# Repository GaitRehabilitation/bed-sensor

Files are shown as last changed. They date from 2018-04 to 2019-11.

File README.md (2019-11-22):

# Bed Sensor

## Background

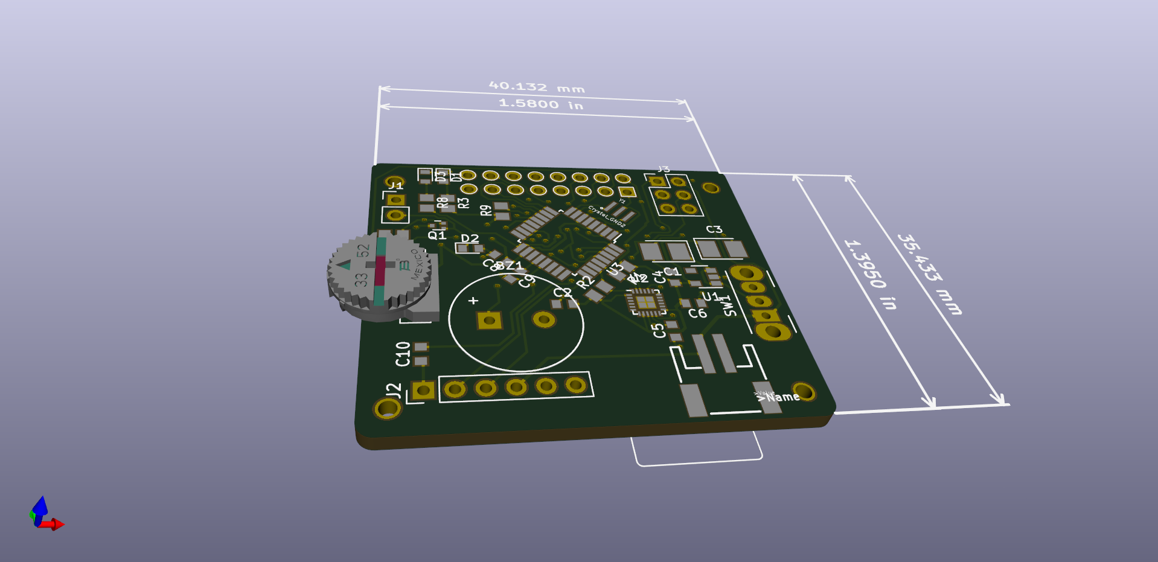
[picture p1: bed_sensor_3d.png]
bed sensor


This sensor is built around the open source schematic of the Ardunio Pro Mini and the seperate parts we're tested sepertly and the final board was printed from [oshPark](https://oshpark.com/). This is an experemential sensor that makes sure patients roll over within a fixed interval. The model uses a state machine with two states: COUNTING_STATE, and a ROTATING_STATE. The counting state samples the direction of the acceleration vector and during the ROTATING_STATE, the arc angle between the current vector and the sampled data from the counting state determins the rotation of the device from the resting state. A average filter is sampled from the current resting angle of the sensor is sampled by taking 20% of the current sample vector and 80% of the current resting angle. This is a mitigation strategy that avoids sampling from sudden movments and affecting the angle of the sensor. The counting state is reset if the devaition from the scalar vector is greater then .35 g's.  

## Programming

Tools:
- [SCONS](https://scons.org/)
- [avrdud](https://www.nongnu.org/avrdude/)
- [avr-gcc](https://gcc.gnu.org/wiki/avr-gcc)
- [minicore](https://github.com/MCUdude/MiniCore)

building cpp code `scons build`. The compiled code produces a hex 

```avrdude -c <programmer> -p atmega328 -b 57600  -U flash:w:main.hex -U lfuse:w:0xff:m -U hfuse:w:0xd1:m -U efuse:w:0xff:m```

![avr fuse](./fuse_bits.png)

[Fuse Calculator](http://eleccelerator.com/fusecalc/fusecalc.php?chip=atmega328p)

## Maintainers

The current maintainers of this repository are:

* Michael Pollind <polli104@mail.chapman.edu>

# License

```
/**
* Copyright 2018 GaitRehabilitation
*
* Licensed under the Apache License, Version 2.0 (the "License");
* you may not use this file except in compliance with the License.
* You may obtain a copy of the License at
*
*     http://www.apache.org/licenses/LICENSE-2.0
*
* Unless required by applicable law or agreed to in writing, software
* distributed under the License is distributed on an "AS IS" BASIS,
* WITHOUT WARRANTIES OR CONDITIONS OF ANY KIND, either express or implied.
* See the License for the specific language governing permissions and
* limitations under the License.
*/

```

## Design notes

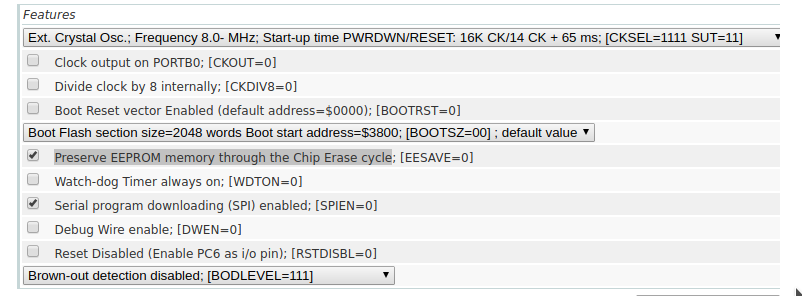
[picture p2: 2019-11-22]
fuse_bits.png

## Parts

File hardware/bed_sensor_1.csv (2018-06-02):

Id | Designator | Package | Quantity | Designation | Supplier and ref
1 | U5 | CFAH0802D-YYH-JP | 1 | CFAH0802D-YYH-JP | https://www.crystalfontz.com/product/cfah0802dyyhjp-8x2-sunlight-readable-character-lcd
2 | BZ1 | PS1240P02BT | 1 | Buzzer | https://www.mouser.com/ProductDetail/TDK/PS1240P02CT3?qs=sGAEpiMZZMs%252b6Ea5iKw4JoP%2fJ%2fqwrEG3
3 | C1 | CP_Tantalum_Case-T_EIA-3528-12_Reflow | 1 | 10uF | https://www.mouser.com/ProductDetail/81-GRM33C80J104KE15D
4 | C2 | C_0603_1608Metric | 1 | 10nF | https://www.mouser.com/ProductDetail/80-C0603X103J4HACTU
5 | C3 | CP_Tantalum_Case-B_EIA-3528-21_Reflow | 1 | 10uF | https://www.mouser.com/ProductDetail/81-GRM33C80J104KE15D
6 | C4,C5 | C_0603_1608Metric | 2 | .1uF | https://www.mouser.com/ProductDetail/81-GRM032R60J104KE5D
7 | C6 | C_0603_1608Metric | 1 | 1uF | https://www.mouser.com/ProductDetail/81-GRM032R60J104KE5D
8 | C7 | C_0603_1608Metric | 1 | 10uF | https://www.mouser.com/ProductDetail/81-GRM33C80J104KE15D
9 | C8,C9,C10 | C_0603_1608Metric | 3 | .1uf | https://www.mouser.com/ProductDetail/81-GRM032R60J104KE5D
10 | D1 | LED_0603_1608Metric | 1 | LED | https://www.mouser.com/ProductDetail/Kingbright/APT1608ZGCK?qs=sGAEpiMZZMuCm2JlHBGefut9Bg6HSmgVetA7n4GwW1U%3d
11 | D2 | D_0603_1608Metric | 1 | D | https://www.mouser.com/ProductDetail/755-RB162VAM-20TR
12 | J1 | PinHeader_1x02_P2.54mm_Vertical | 1 | Conn_01x02
13 | J2 | PinHeader_1x06_P2.54mm_Vertical | 1 | Conn_01x06
14 | J3 | PinHeader_2x03_P2.54mm_Vertical | 1 | ISP
15 | JP1 | SolderJumper-2_P1.3mm_Open_Pad1.0x1.5mm | 1 | Jumper_NO_Small
16 | L1 | L_Taiyo-Yuden_NR-40xx | 1 | 10uH | https://www.mouser.com/ProductDetail/Murata-Electronics/LQH32CN100K53L
17 | Q1 | SOT-723 | 1 | 2N2219 | https://www.mouser.com/ProductDetail/ON-Semiconductor/NSVMMBT2222AM3T5G
18 | Q2,Q3 | SOT-23 | 2 | BSS138 | https://www.mouser.com/ProductDetail/ON-Semiconductor-Fairchild/BSS138?qs=sGAEpiMZZMvlOED0T0kTWl5MKyjMqq%2fg
19 | R1,R2,R3,R6,R7,R9 | R_0805_2012Metric | 6 | 10k | https://www.mouser.com/ProductDetail/603-RC0805FR-0710KL
20 | R4 | R_0805_2012Metric | 1 | 1K | https://www.mouser.com/ProductDetail/603-RC0805JR-071KL
21 | R5 | R_0805_2012Metric | 1 | 220 | https://www.mouser.com/ProductDetail/Vishay/CRCW0805220RFKEAC
22 | R8 | R_0805_2012Metric | 1 | 330 | https://www.mouser.com/ProductDetail/652-CR0805-FX3300GLF
23 | RV1 | Potentiometer_Trimmer_ACP_CA9h2.5_Vertical_Px2.5mm_Py5.0mm | 1 | 10K | https://www.amazon.com/MCIGICM-potentiometer-assortment-Breadboard-Potentiometer/dp/B07C3XHVXV?s=industrial
24 | SW1 | SW_CuK_OS102011MA1QN1_SPDT_Angled | 1 | SW_SPST | https://www.mouser.com/ProductDetail/611-OS102011MA1QN1
25 | U1 | SOT-23-5 | 1 | MIC5205-3.3 | https://www.mouser.com/ProductDetail/Microchip-Technology-Micrel/MIC5205-33YM5-TR
26 | U2 | QFN-24-1EP_3x3mm_P0.4mm_EP1.75x1.6mm | 1 | MPU-9250 | https://www.mouser.com/ProductDetail/TDK-InvenSense/MPU-9250
27 | U3 | SOIC-14_3.9x8.7mm_P1.27mm | 1 | TXB0104D | https://www.mouser.com/ProductDetail/Texas-Instruments/TXB0104D
28 | U4 | SOT-363_SC-70-6 | 1 | LTC3525-5 | https://www.mouser.com/ProductDetail/Analog-Devices-Linear-Technology/LTC3525ESC6-5TRPBF
29 | Y1 | OSC_CSTCE8M00G55-R0 | 1 | Crystal_GND2 | https://www.mouser.com/ProductDetail/81-CSTCE8M00G55-R0
30 | D3 | LED_0603_1608Metric_Pad0.67x1.00mm_HandSolder | 1 | LD271 | https://www.mouser.com/ProductDetail/Kingbright/APT1608VBC-D?qs=sGAEpiMZZMuCm2JlHBGefut9Bg6HSmgVsfyCYNObiTs%3d
31 | J4 | JSTPH2 | 1 | Conn_01x02 | https://www.adafruit.com/product/1769
32 | U6 | TQFP-32_7x7mm_Pitch0.8mm | 1 | ATMEGA328-AU | https://www.mouser.com/ProductDetail/556-ATMEGA328-AU

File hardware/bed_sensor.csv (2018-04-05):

Id | Designator | Package | Quantity | Designation | Supplier and ref
1 | J1 | JSTPH2 | 1 | Conn_01x02 | https://www.adafruit.com/product/1769
2 | J2 | PinHeader_1x06_P2.54mm_Horizontal | 1 | Conn_01x06
3 | J3 | PinHeader_1x02_P2.54mm_Vertical | 1 | Conn_01x02 | https://www.adafruit.com/product/1201
4 | SW1 | SW_CuK_OS102011MA1QN1_SPDT_Angled | 1 | SW_SPST | https://www.mouser.com/ProductDetail/611-OS102011MA1QN1
5 | uP1 | ArduProMini | 1 | ARDUPROMINI
6 | RV1 | Potentiometer_ACP_CA6-H2,5_Horizontal | 1 | 10K | https://www.mouser.com/ProductDetail/Bourns/3310C-001-103L
7 | D1 | D_DO-35_SOD27_P7.62mm_Horizontal | 1 | D
8 | Q1 | TO-92_Inline | 1 | 2N2219
9 | R1 | R_Axial_DIN0207_L6.3mm_D2.5mm_P7.62mm_Horizontal | 1 | 220
10 | R2 | R_Axial_DIN0207_L6.3mm_D2.5mm_P7.62mm_Horizontal | 1 | 1K
11 | BZ1 | MagneticBuzzer_Kingstate_KCG0601 | 1 | Buzzer | https://www.mouser.com/ProductDetail/TDK/PS1240P02CT3?qs=sGAEpiMZZMs%252b6Ea5iKw4JoP%2fJ%2fqwrEG3
12 | DS1 | NHD-0216HZ-FSW-FBW-33V3C | 1 | WC1602A | https://www.mouser.com/ProductDetail/Newhaven-Display/NHD-0216HZ-FSW-FBW-33V3C
13 | J4 | PinSocket_1x08_P2.54mm_Vertical | 1 | Conn_01x08 | https://www.amazon.com/MPU-6050-MPU6050-Accelerometer-Gyroscope-Converter/dp/B008BOPN40

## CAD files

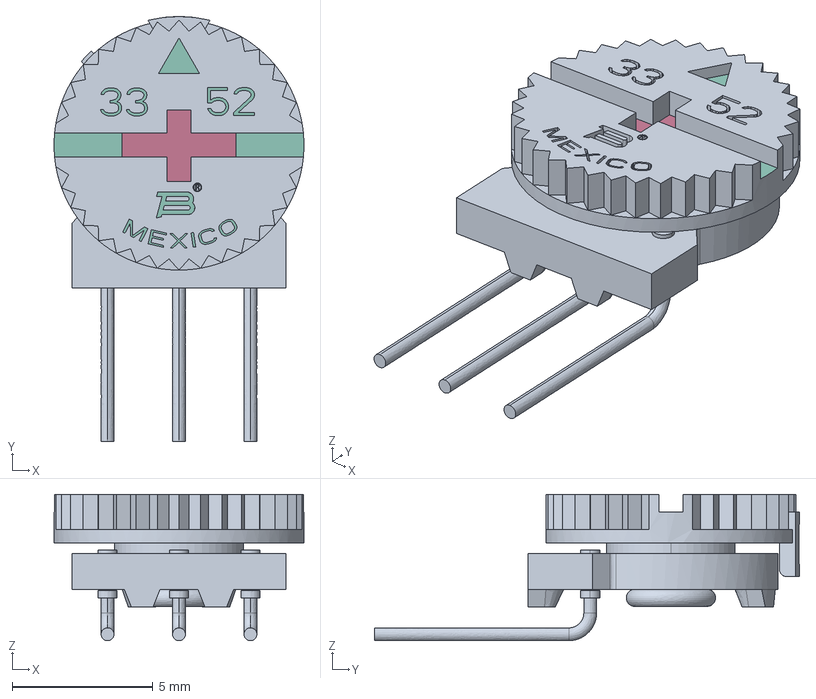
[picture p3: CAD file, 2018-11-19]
hardware/3352W001XXX.stp
8.89 x 15.1 x 5.21 mm

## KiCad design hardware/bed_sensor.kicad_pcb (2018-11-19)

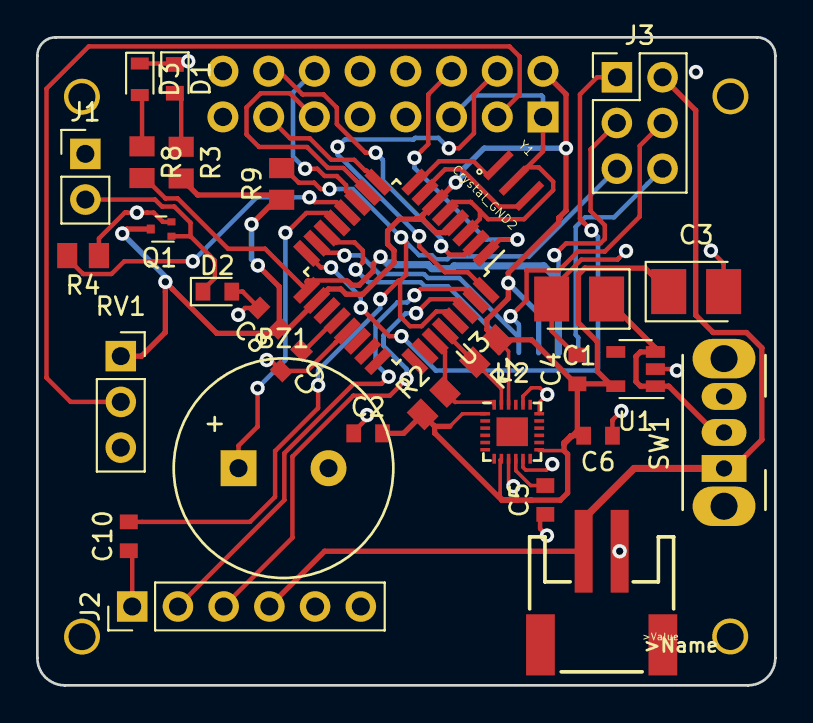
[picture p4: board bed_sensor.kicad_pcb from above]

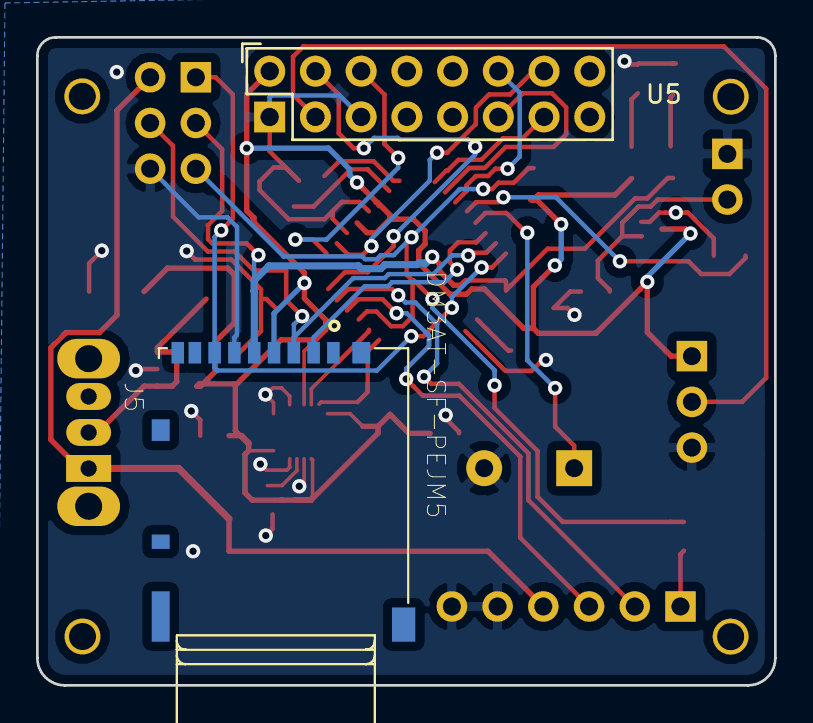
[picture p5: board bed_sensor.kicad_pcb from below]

Board: 2 copper layers, 41.0 x 36.0 mm, 32 parts (2 on the bottom side), 31 nets.

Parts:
BZ1: Buzzer; PS1240P02BT
C1: 10uF; CP_Tantalum_Case-T_EIA-3528-12_Reflow
C2: 10nF; C_0603_1608Metric
C3: 10uF; CP_Tantalum_Case-B_EIA-3528-21_Reflow
C4, C5, C6: .1uF; C_0603_1608Metric
C8, C9, C10: .1uf; C_0603_1608Metric
D1: LED; LED_0603_1608Metric
D2: D; D_0603_1608Metric
D3: LD271; LED_0603_1608Metric_Pad0.67x1.00mm_HandSolder
J1: Conn_01x02; PinHeader_1x02_P2.54mm_Vertical
J2: Conn_01x06; PinHeader_1x06_P2.54mm_Vertical
J3: ISP; PinHeader_2x03_P2.54mm_Vertical
J4: Conn_01x02; JSTPH2
J5: DM3AT-SF-PEJM5; HRS_DM3AT-SF-PEJM5
Q1: 2N2219; SOT-723
R1, R2, R3, R9: 10k; R_0805_2012Metric
R4: 1K; R_0805_2012Metric
R8: 330; R_0805_2012Metric
RV1: 10K; PinSocket_1x03_P2.54mm_Vertical
SW1: SW_SPST; SW_CuK_OS102011MA1QN1_SPDT_Angled
U1: MIC5205-3.3; SOT-23-5
U2: MPU-9250; QFN-24-1EP_3x3mm_P0.4mm_EP1.75x1.6mm
U3: ATMEGA328-AU; TQFP-32_7x7mm_P0.8mm
U5: CFAH0802D-YYH-JP
Y1: Crystal_GND2; OSC_CSTCE8M00G55-R0

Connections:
+3V3: C2.2, C3.1, C4.1, C6.2, C8.1, J5.4, Q1.3, R1.1, R2.1, R3.2, R9.1, RV1.1, U1.5, U2.1, U2.8, U2.13, U2.22, U3.4, U3.6, U3.18, U5.2
/Ardunio/DTR: C10.1, J2.1
/Ardunio/RESET: C10.2, J3.5, R9.2, U3.29
/Ardunio/RX1: J2.3, U3.30
/Ardunio/TX0: J2.2, U3.31
Buzzer: BZ1.1, U3.13
CS: J5.2, U3.14
DB4: U3.10, U5.11
DB5: U3.11, U5.12
DB6: U3.9, U5.13
DB7: U3.2, U5.14
Display_Enable: U3.1, U5.6
GND: BZ1.2, C1.2, C2.1, C3.2, C4.2, C5.1, C6.1, C8.2, C9.2, D1.1, D2.2, D3.1, J1.1, J2.5, J2.6, J3.6, J4.1, J5.6, RV1.3, U1.2, U2.9, U2.11, U2.18, U2.20, U3.3, U3.5, U3.21, U5.1, U5.5, Y1.2
MISO: J3.1, J5.7, U3.16
MOSI: J3.4, J5.3, U3.15
unnamed: C1.1, SW1.2, U1.1, U1.3
unnamed: C5.2, U2.10
unnamed: C9.1, U3.20
unnamed: D1.2, R3.1
unnamed: D2.1, J1.2, Q1.1
unnamed: D3.2, R8.1
unnamed: Q1.2, R4.1
unnamed: RV1.2, U5.3
unnamed: U3.7, Y1.3
unnamed: U3.8, Y1.1
RS: U3.32, U5.4
SCK: J3.3, J5.5, R8.2, U3.17
SCL_MPU: R1.2, U2.23, U3.28
SDA_MPU: R2.2, U2.24, U3.27
VCC: J2.4, J3.2, J4.2, SW1.1
Vibration: R4.2, U3.12

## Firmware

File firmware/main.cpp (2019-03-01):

#define __AVR_ATmega328__ 1

#include <Arduino.h>
#include <Wire.h>
#include <SPI.h>
#include <SdFat.h>

#include <LiquidCrystal.h>

#define COUNTING_STATE 0
#define ROTATE_STATE 1

#define TARGET_ANGLE 50.0f //degreese
#define TIME 7200000       //milliseconds
#define REMIND_TIME 15000

// PINS ------------------------------------------------------
const int MPU_addr = 0x68;
const int rs = 2, en = 3, d4 = 6, d5 = 7, d6 = 5, d7 = 4;
const int piezoPin = 9;
const int chipSelect = 10;

const char REPOS_MSG[] = {"Re-Pos"};
const char META_FILE[] = {"META.bin"};
// PINS ------------------------------------------------------

LiquidCrystal lcd(rs, en, d4, d5, d6, d7);

unsigned long previous_time = 0;
unsigned long lcd_refresh = 0;
unsigned long display_time = 0;
unsigned long meta_update_time = 0;

float restingX, restingY, restingZ;
float rotationX, rotationY, rotationZ;
float scaledX, scaledY, scaledZ;
float movingAvg = 0.0f;
int count = 0;

byte state = 0;

// LOGGING DATA -----------------------------------------------------------
const uint32_t LOG_INTERVAL_USEC = 10000;
const uint8_t BUFFER_BLOCK_COUNT = 10;
const uint32_t FILE_BLOCK_COUNT = 256000;
const uint8_t ACCEL_DIM = 3;
const uint8_t GYRO_DIM = 3;

//size of the queue
const uint8_t QUEUE_DIM = BUFFER_BLOCK_COUNT + 1;
// Index of last queue location.
const uint8_t QUEUE_LAST = QUEUE_DIM - 1;

bool reset_buzzer = false;
bool reminder_buzzer = false;
bool reset_on_move = false;

//sdfat
SdFat sd;
SdBaseFile binFile;
// SdBaseFile metaFile;
char fileName[13];

struct data_t
{
  uint32_t time;
  int16_t accel[ACCEL_DIM];
  int16_t gyro[GYRO_DIM];
  int16_t temp;
  uint8_t meta;
};

// DATA BLOCK 512 bytes --------------------------------------------------------------------
// Number of data records in a block.
const uint16_t DATA_DIM = (512 - 2) / sizeof(data_t);

//Compute fill so block size is 512 bytes.  FILL_DIM may be zero.
const uint16_t FILL_DIM = 512 - 2 - DATA_DIM * sizeof(data_t);

//data
struct block_t
{
  uint16_t count;
  data_t data[DATA_DIM];
  uint8_t fill[FILL_DIM];
};

bool isResting(float x, float y, float z);
void createBin();
void sdFail(const char *);
float arcAngle(float tx, float ty, float tz, float fx, float fy, float fz);
void acquireData(data_t *data);

void setup()
{
  // wdt_enable(WDTO_2S);
  lcd.begin(16, 2);
  if (!sd.begin(chipSelect, SD_SCK_MHZ(50)))
  {
    sdFail("REQ SD");
  }
  pinMode(piezoPin, OUTPUT);

  restingX = .01f;
  restingY = .01f;
  restingZ = .01f;
  rotationX = .1f;
  rotationY = .01f;
  rotationZ = .01f;

  Wire.begin();
  Wire.beginTransmission(MPU_addr);
  Wire.write(0x6B); // PWR_MGMT_1 register
  Wire.write(0);    // set to zero (wakes up the MPU-6050)
  Wire.endTransmission(true);

  Wire.beginTransmission(MPU_addr);
  Wire.write(0x1C);
  Wire.write(B00001000); //here is the byte for sensitivity (8g here)
  Wire.endTransmission(true);


  Wire.beginTransmission(MPU_addr);
  Wire.write(0x1B);
  Wire.write(B00101000); //here is the byte for sensitivity (1000 degree sec)
  Wire.endTransmission(true);

}

void loop()
{
  createBin();
  
  // Allocate extra buffer space.
  block_t block[BUFFER_BLOCK_COUNT - 1];
  block_t *emptyStack[BUFFER_BLOCK_COUNT];
  block_t *fullQueue[QUEUE_DIM];

  block_t *curBlock = 0;

  uint8_t emptyTop;
  uint8_t minTop;

  uint8_t fullHead = 0;
  uint8_t fullTail = 0;

  emptyStack[0] = (block_t *)sd.vol()->cacheClear();
  if (emptyStack[0] == 0)
  {
    return;
  }
  // Put rest of buffers on the empty stack.
  for (int i = 1; i < BUFFER_BLOCK_COUNT; i++)
  {
    emptyStack[i] = &block[i - 1];
  }
  emptyTop = BUFFER_BLOCK_COUNT;
  minTop = BUFFER_BLOCK_COUNT;

  // Start a multiple block write.
  if (!sd.card()->writeStart(binFile.firstBlock()))
  {
    return;
  }

  uint32_t bn = 0;
  uint32_t maxLatency = 0;
  uint32_t logTime = micros();
  display_time = millis();

  while (1)
  {
    // --------------------------- Recording Data ----------------------------------------------

    // Time for next data record.
    logTime += LOG_INTERVAL_USEC;

    if (curBlock == 0 && emptyTop != 0)
    {
      curBlock = emptyStack[--emptyTop];
      if (emptyTop < minTop)
      {
        minTop = emptyTop;
      }
      curBlock->count = 0;
    }
    int32_t delta;

    do
    {
      delta = micros() - logTime;
    } while (delta < 0);

    if (curBlock != 0)
    {
      acquireData(&curBlock->data[curBlock->count++]);
      if (curBlock->count == DATA_DIM)
      {
        fullQueue[fullHead] = curBlock;
        fullHead = fullHead < QUEUE_LAST ? fullHead + 1 : 0;
        curBlock = 0;
      }
    }

    switch (state)
    {
    case ROTATE_STATE:
    {
      float angle = arcAngle(restingX, restingY, restingZ, rotationX, rotationY, rotationZ);

      if ((millis() - lcd_refresh) > 500)
      {
        lcd.clear();
        lcd.setCursor(0, 0);
        lcd.print(100.0f * (angle / TARGET_ANGLE));
        lcd.print('%');
        lcd.setCursor(0, 1);
        lcd.print(REPOS_MSG);
        lcd_refresh = millis();
      }
      if ((millis() - previous_time) > REMIND_TIME)
      {
        tone(piezoPin, 1000, 500);
        previous_time = millis();
        reset_buzzer = true;
      }

      if (angle > TARGET_ANGLE)
      {
        state = COUNTING_STATE;
        tone(piezoPin, 200, 500);
        delay(1000);
        tone(piezoPin, 200, 500);
        reminder_buzzer = true;
        previous_time = millis();
        display_time = millis();
      }
      
      rotationX = .2f * scaledX + (1 - .2f) * rotationX;
      rotationY = .2f * scaledY + (1 - .2f) * rotationY;
      rotationZ = .2f * scaledZ + (1 - .2f) * rotationZ;
    
    }
    break;
    case COUNTING_STATE:
    {
    

      if((millis() - display_time) > 10000){
        lcd.noDisplay();
      }
      else{
        if ((millis() - lcd_refresh) > 1000)
        {
          lcd.display();
          lcd.clear();
          lcd.setCursor(0, 0);
          lcd.print((millis() - previous_time) / 1000);
          lcd.print('/');
          lcd.setCursor(0, 1);
          lcd.print(TIME / 1000);
          lcd_refresh = millis();
        }
      }

      if ((millis() - previous_time) > TIME)
      {
        lcd.display();
        tone(piezoPin, 1000, 500);
        state = ROTATE_STATE;
        rotationX = restingX;
        rotationY = restingY;
        rotationZ = restingZ;
      }

      movingAvg = (movingAvg * .9f) + (abs(1.0f - sqrt((scaledX * scaledX) + (scaledY * scaledY) + (scaledZ * scaledZ))) * (1 - .9f));
      if (movingAvg > 0.35f)
      {
        reset_on_move = true;
        previous_time = millis();
        display_time = millis();
      }
      restingX = .2f * scaledX + (1 - .2f) * restingX;
      restingY = .2f * scaledY + (1 - .2f) * restingY;
      restingZ = .2f * scaledZ + (1 - .2f) * restingZ;
    
    }
    break;
    }

    if (fullHead != fullTail && !sd.card()->isBusy())
    {
      // Get address of block to write.
      block_t *pBlock = fullQueue[fullTail];
      fullTail = fullTail < QUEUE_LAST ? fullTail + 1 : 0;
      // Write block to SD.
      uint32_t usec = micros();
      if (!sd.card()->writeData((uint8_t *)pBlock))
      {
        sdFail("Write Fail");
      }
      usec = micros() - usec;
      if (usec > maxLatency)
      {
        maxLatency = usec;
      }
      // Move block to empty queue.
      emptyStack[emptyTop++] = pBlock;
      bn++;
      if (bn == FILE_BLOCK_COUNT)
      {
        // file full so create a new bin file and continue
        break;
      }
    }
  }
}

float arcAngle(float tx, float ty, float tz, float fx, float fy, float fz)
{
  if(abs(tx - fx) < .0001f && abs(ty - fy) < .0001f && abs(tz - fz) < .0001f)
    return 10.0f;
  float tmag = sqrt((tx * tx) + (ty * ty) + (tz * tz)) + .1f;
  float fmag = sqrt((fx * fx) + (fy * fy) + (fz * fz)) + .1f;
  tx = tx/tmag;
  ty = ty/tmag;
  tz = tz/tmag;

  fx = fx/fmag;
  fy = fy/fmag;
  fz = fz/fmag;

  return acos((tx * fx + ty * fy + tz * fz) / (tmag * fmag)) * (180.0f / PI);
}

bool isResting(float x, float y, float z)
{
  return abs(1.0f - sqrt((x * x) + (y * y) + (z * z))) < .01f;
}

void createBin()
{
  // max number of blocks to erase per erase call
  const uint32_t ERASE_SIZE = 262144L;
  uint32_t bgnBlock, endBlock;
  while (true)
  {
    sprintf_P(fileName, PSTR("LOG%05u.BIN"), count);
    if (count > 65533) //There is a max of 65534 logs
    {
      sdFail("Max log");
    }
    if (!sd.exists(fileName))
    {
      // create a new bin file if exsists
      binFile.close();
      if (!binFile.createContiguous(fileName, 512 * FILE_BLOCK_COUNT))
      {
        sdFail("CRT CONT");
      }

      // Get the address of the file on the SD.
      if (!binFile.contiguousRange(&bgnBlock, &endBlock))
      {
        sdFail("CRT CONT");
      }

      // Flash erase all data in the file.
      uint32_t bgnErase = bgnBlock;
      uint32_t endErase;
      while (bgnErase < endBlock)
      {

        endErase = bgnErase + ERASE_SIZE;
        if (endErase > endBlock)
        {
          endErase = endBlock;
        }
        if (!sd.card()->erase(bgnErase, endErase))
        {
          sdFail("Ers Fail");
        }
        bgnErase = endErase + 1;
      }

      break;
    }
    count++;
  }
}

void sdFail(const char *str)
{
  lcd.clear();
  lcd.setCursor(0, 1);
  lcd.print("SD CARD");
  lcd.setCursor(0, 0);
  lcd.print(str);

  while (1)
    ;
}

void acquireData(data_t *data)
{
  Wire.beginTransmission(MPU_addr);
  Wire.write(0x3B); // starting with register 0x3B (ACCEL_XOUT_H)
  Wire.endTransmission(false);
  Wire.requestFrom(MPU_addr, 14, true);            // request a total of 14 registers
  data->accel[0] = Wire.read() << 8 | Wire.read(); // 0x3B (ACCEL_XOUT_H) & 0x3C (ACCEL_XOUT_L)
  data->accel[1] = Wire.read() << 8 | Wire.read(); // 0x3D (ACCEL_YOUT_H) a& 0x3E (ACCEL_YOUT_L)
  data->accel[2] = Wire.read() << 8 | Wire.read(); // 0x3F (ACCEL_ZOUT_H) & 0x40 (ACCEL_ZOUT_L)
  data->temp = Wire.read() << 8 | Wire.read();     // 0x41 (TEMP_OUT_H) & 0x42 (TEMP_OUT_L)
  data->gyro[0] = Wire.read() << 8 | Wire.read();  // 0x43 (GYRO_XOUT_H) & 0x44 (GYRO_XOUT_L)
  data->gyro[1] = Wire.read() << 8 | Wire.read();  // 0x45 (GYRO_YOUT_H) & 0x46 (GYRO_YOUT_L)
  data->gyro[2] = Wire.read() << 8 | Wire.read();  // 0x47 (GYRO_ZOUT_H) & 0x48 (GYRO_ZOUT_L)
  data->time = micros();
  data->meta = 0;
  if (reset_buzzer)
    data->meta |= (1 << 0);
  if (reminder_buzzer)
    data->meta |= (1 << 1);
  if (reset_on_move)
    data->meta |= (1 << 2);

  reset_buzzer = false;
  reminder_buzzer = false;
  reset_on_move = false;

  scaledX = ((float)data->accel[0]) / 8192.0;
  scaledY = ((float)data->accel[1]) / 8192.0;
  scaledZ = ((float)data->accel[2]) / 8192.0;
}

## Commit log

2018-04-05 add csv
    [bed_sensor.csv, bed_sensor.kicad_pcb, bed_sensor.sch]
2018-04-05 fixed layout
    [bed_sensor.csv, bed_sensor.kicad_pcb]
2018-04-05 updated csv
    [bed_sensor.csv, bed_sensor.kicad_pcb]
2018-04-06 twekaed paths
    [bed_sensor.kicad_pcb]
2018-04-06 added measurements
    [bed_sensor.kicad_pcb]
2018-06-01 added CFAH0802d
    [Ardunio.sch, _saved_bed_sensor.sch, ardunio.sch, bed_sensor.sch]
2018-06-02 updated schematic
    [_saved_Ardunio.sch, _saved_bed_sensor.sch, bed_sensor.kicad_pcb, bed_sensor.sch]
2018-06-02 updated design
    [Ardunio.sch, _saved_Ardunio.sch, _saved_bed_sensor.sch, bed_sensor.kicad_pcb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]
2018-06-12 updated pcb layout
    [bed_sensor.kicad_pcb, bed_sensor.sch]
2018-06-13 corrected pinout for NHD display
    [bed_sensor.kicad_pcb, bed_sensor.sch]
2018-06-19 added SD card
    [Ardunio.sch, bed_sensor.kicad_pcb, bed_sensor.sch]
2018-06-22 added toggle button to side of board
    [bed_sensor.kicad_pcb, bed_sensor.sch]
2018-08-30 flipped screen
    [Ardunio.sch, bed_sensor.kicad_pcb, bed_sensor.sch]
2018-08-30 cleaned up board
    [bed_sensor.kicad_pcb]
2018-08-30 tweaked layout
    [bed_sensor.kicad_pcb]
2018-08-30 fixed silk and mask for screen
    [bed_sensor.kicad_pcb]
2018-08-30 shifted components arround to accomidate buzzer
    [bed_sensor.kicad_pcb]
2018-09-19 updated layout
    [bed_sensor.kicad_pcb]
2018-09-24 updated layout for thumb pot
    [bed_sensor.kicad_pcb, bed_sensor.sch]
2018-11-19 modified design slightly and fixed problems with layout
    [3352W001XXX.stp, Ardunio.sch, ardunio.sch, bed_sensor.csv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]
2018-11-19 updated schematic removed old kicad design
    [bed_sensor.sch, bed_sensor_1.kicad_pcb]
2018-11-20 tweaked firmware for angle
    [Ardunio.sch, bed_sensor.sch]
